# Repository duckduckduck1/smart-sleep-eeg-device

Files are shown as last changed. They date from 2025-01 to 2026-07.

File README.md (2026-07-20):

# Устройство ЭЭГ «Умного сна»

Прошивка и схемотехника ЭЭГ-устройства для нейробиологической лаборатории,
которая исследует сон на мышах.

Устройство снимает сигнал ЭЭГ аналоговым трактом на **MAX30003**, отдаёт его по
Bluetooth через модуль **JDY-16** и принимает обратно команды управления
фотобиомодуляцией — светом, которым воздействуют на животное. На другом конце —
[приложение оператора](https://github.com/duckduckduck1/smart-sleep-eeg-app),
которое пишет эксперимент на диск.

## Зачем это

Готовых ЭЭГ-регистраторов под мышь с нужным сочетанием требований нет: малый
вес на голове животного, автономное питание, беспроводная передача и
управляемый источник света в одном устройстве. Поэтому и плата, и прошивка
свои.

Репозиторий закрывает всё, что относится к железу: схемы трёх плат, прошивку
микроконтроллера и контракт обмена с приложением.

## Состав

Три платы, соединённые последовательно:

```text
Head_Mouse            MAX_V5              EEG_MASTER_REV2
(на голове мыши)  →  (аналоговый тракт) →  (МК, BLE, питание)  →  BLE → ПК
   электроды           MAX30003              STM32F103 + JDY-16
```

- **МК** — STM32F103C8T6.
- **Аналоговый тракт** — MAX30003, 250 Гц, связь по SPI.
- **Радио** — JDY-16 на UART, 9600 бод.
- **Питание** — литиевый аккумулятор, зарядка TP4056, стабилизаторы на 3,3 и
  1,8 В.

## С чего начать

**Чтобы собрать прошивку** нужны Visual Studio с
[VisualGDB](https://visualgdb.com/) и программатор ST-Link. Решение —
`firmware/visualgdb/smart-sleep-eeg-device.sln`, заливка по SWD.

При первой прошивке на новой машине почти наверняка потребуется поставить
драйвер WinUSB на ST-Link — как именно, описано
в [docs/firmware.md](docs/firmware.md#прошивка-не-идёт-error-open-failed).

**Чтобы открыть схемы** нужен Altium Designer. Проекты — в `hardware/`.

**Чтобы менять назначение ног** нужен
[STM32CubeMX](https://www.st.com/en/development-tools/stm32cubemx.html), файл
`firmware/EEG_sample.ioc`. Но прежде прочитайте про генерацию кода
в [docs/firmware.md](docs/firmware.md#не-перегенерировать-код-из-ioc): часть
логики дописана руками и генератор её перезапишет.

## Структура репозитория

```text
firmware/            прошивка STM32F103
  Core/              код от CubeMX и дописанная логика
  Drivers/           HAL и CMSIS от ST
  visualgdb/         проект VisualGDB и драйвер MAX30003
  EEG_sample.ioc     конфигурация CubeMX
hardware/            схемотехника, три проекта Altium
  EEG_MASTER_REV2/   основная плата: STM32, JDY-16, питание
  MAX_V5/            аналоговый тракт на MAX30003
  EEG_Head_Mouse V1/ головной модуль с электродами
docs/                документация
  firmware.md        сборка, распиновка, протокол, особенности
  hardware.md        платы и связь между ними
  datasheets/        документация на MAX30003 и STM32F103
```

## Документация

- [docs/firmware.md](docs/firmware.md) — как собирается прошивка, распиновка,
  протокол обмена с приложением, подводные камни.
- [docs/hardware.md](docs/hardware.md) — что за платы, из чего собраны, как
  связаны, что хранится в проектах Altium, а что нет.
- [CONTRIBUTING.md](CONTRIBUTING.md) — ветки, коммиты, что не коммитить.
- [Формат данных эксперимента](https://github.com/duckduckduck1/smart-sleep-eeg-app/blob/main/docs/data-format.md)
  — на стороне приложения: как декодировать отсчёты в микровольты. Контракт
  общий, поэтому здесь он не дублируется.

## Если что-то не работает

- **Проект не собирается после переноса файлов** — проверьте, что папка
  `firmware/` цела: проект VisualGDB тянет исходники относительными путями на
  два уровня вверх от себя.
- **Altium жалуется на недостающие библиотеки** — стандартные библиотеки
  компонентов в репозитории не хранятся, см.
  [docs/hardware.md](docs/hardware.md#что-лежит-в-проектах-а-что-нет). На уже
  размещённые элементы это не влияет.
- **Не прошивается, `Error: open failed`** — не установлен драйвер WinUSB на
  ST-Link. Лечится через Zadig, см.
  [docs/firmware.md](docs/firmware.md#прошивка-не-идёт-error-open-failed).
- **Устройство не находится по Bluetooth** — имя задаётся прошивкой командой
  `AT+NAMEEEG` при старте; ищите `EEG`.

Не нашли ответа — заведите
[issue](https://github.com/duckduckduck1/smart-sleep-eeg-device/issues).

## Кто поддерживает

Проект ведёт [@duckduckduck1](https://github.com/duckduckduck1) для конкретной
лаборатории. Изменения — через pull request, правила
в [CONTRIBUTING.md](CONTRIBUTING.md).

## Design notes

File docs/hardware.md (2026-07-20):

# Платы устройства

Описание трёх проектов Altium из `hardware/`: что за плата, из чего собрана и
как связана с остальными.

Состав восстановлен по схемам и библиотекам проектов. Где сведений в файлах не
нашлось, это отмечено прямо — лучше пробел, чем догадка, выданная за факт.

## Как платы связаны

```text
Head_Mouse            MAX_V5              EEG_MASTER_REV2
(на голове мыши)  →  (аналоговый тракт) →  (МК, BLE, питание)  →  BLE → ПК
   электроды           MAX30003              STM32F103 + JDY-16
```

Сигнал идёт от электродов на головном модуле в аналоговый тракт MAX30003,
оттуда по SPI в STM32, а из него по UART в модуль JDY-16 и дальше по BLE в
[приложение оператора](https://github.com/duckduckduck1/smart-sleep-eeg-app).

## EEG_MASTER_REV2 — основная плата

Несёт микроконтроллер, радиомодуль и питание. Схема разбита на четыре листа.

| лист | что на нём |
|---|---|
| `Main.SchDoc` | сборка листов, отладочный разъём SWD |
| `STM32.SchDoc` | STM32F103, модуль **JDY-16**, транслятор уровней **BSS138**, светодиод |
| `Power.SchDoc` | зарядка **TP4056**, стабилизаторы **RT9013-33GB** (3,3 В) и **RT9013-18GB** (1,8 В) |
| `Connectors.SchDoc` | разъёмы **BM10B-SRSS-TB** (JST, 10 контактов) к плате MAX30003 |

Два стабилизатора не случайны: цифровая часть MAX30003 питается от 1,8 В, а
STM32 и радиомодуль — от 3,3 В. Отсюда же и BSS138 — согласование уровней между
доменами.

Наличие TP4056 означает питание от литиевого аккумулятора с зарядкой по USB.

Файлы плат: `EEG_Master_Rev2.PcbDoc`, `EEG_MASTER_REV2(2).PcbDoc`,
`ALL_PCB.PcbDoc`. Какая из трёх версий актуальна — из файлов не следует.

## MAX_V5 — аналоговый тракт

Плата с **MAX30003**: снимает сигнал с электродов и отдаёт его по SPI.
Схема — `Sheet2.SchDoc`, плата — `PCB2.PcbDoc`.

Параметры тракта, от которых зависит перевод отсчётов в микровольты
(`V_REF = 1.0 В`, `GAIN = 160`), описаны на стороне приложения:
[docs/data-format.md](https://github.com/duckduckduck1/smart-sleep-eeg-app/blob/main/docs/data-format.md).

## EEG_Head_Mouse V1 — головной модуль

Плата, которая ставится на голову животного и держит электроды.
Схема — `Sheet1.SchDoc`, плата — `PCB1.PcbDoc`.

Из схемы состав вытащить не удалось — текстовых обозначений в файле нет. По
библиотекам проекта видно, что используются микроразъёмы **SAMTEC** серии DWM
(`DWM-03-X-X-S-X`, `DWM-04-60-G-S-625`) — типовой выбор для съёмного соединения
с головным имплантом.

## Что лежит в проектах, а что нет

В репозитории то, без чего проект не открыть и плату не повторить: схемы,
платы, файлы проектов, BOM, задания вывода и библиотеки под конкретные
компоненты.

Не хранится то, что Altium делает сам:

| не хранится | почему |
|---|---|
| `History/` | собственный контроль версий Altium — снимки тех же файлов, которые уже версионирует git |
| `Project Outputs for *` | герберы, сверловка, PDF — генерируются из проекта |
| `Project Logs for *` | журналы работы Altium |
| `__Previews/` | миниатюры предпросмотра |
| `IntegratedLibrary/` | стандартные библиотеки резисторов, конденсаторов, пассивки, транзисторов — общие, ставятся с Altium |

Из-за этого при первом открытии проекта Altium может пожаловаться на
недостающие библиотеки для типовых компонентов. На уже размещённые элементы это
не влияет: их данные лежат в самих схемах и платах. Библиотеки нужны только
чтобы **добавлять новые** типовые компоненты — тогда подключите стандартные
библиотеки Altium.

## Даташиты

`docs/datasheets/` — документация на две ключевые микросхемы:

- `max30003.pdf` — аналоговый тракт, карта регистров, формат FIFO;
- `stm32f103c8.pdf` — микроконтроллер.

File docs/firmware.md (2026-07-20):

# Прошивка

Подробности по прошивке STM32F103: как собирается, распиновка, обмен с
приложением оператора и особенности, о которых стоит знать заранее.

Общее описание проекта — в [README.md](../README.md), платы —
в [hardware.md](hardware.md).

## Как собирается

Два инструмента, у каждого своя роль:

1. **STM32CubeMX** — назначение ног и периферии. По файлу `EEG_sample.ioc` он
   генерирует код инициализации на HAL: `Core/Src/gpio.c`, `spi.c`, `tim.c`,
   `usart.c`, `dma.c` и каркас `main.c`.
2. **VisualGDB в Visual Studio** — сборка и прошивка. Сгенерированный проект
   импортируется сюда, и дальше вся работа идёт в нём.

Решение — `firmware/visualgdb/smart-sleep-eeg-device.sln`. Проект собирает
исходники из `firmware/Core/`, поднимаясь на два уровня вверх от своего файла,
плюс лежащий рядом драйвер `max30003.c`. Прошивка заливается по SWD
(ноги PA13/PA14).

> **STM32CubeIDE в работе не используется.** Файлы `.cproject`, `.project`,
> `.settings` и `.mxproject` — побочный продукт CubeMX: он создаёт их, потому
> что в качестве тулчейна выбран CubeIDE. Собрать по ним проект не получится
> (драйвер MAX30003 не входит в их пути включения), но это ничего не значит —
> ими никто не пользуется. Удалять их тоже незачем: CubeMX создаст их заново.

### Что понадобится

| | где взять |
|---|---|
| **STM32CubeMX** | [st.com](https://www.st.com/en/development-tools/stm32cubemx.html) — бесплатно, нужна регистрация |
| **Visual Studio** | достаточно редакции Community |
| **VisualGDB** | [visualgdb.com](https://visualgdb.com/) — платный, есть пробный период и отдельная лицензия для некоммерческого использования |
| **ST-Link** | программатор, подключается к PA13/PA14 |

## Прошивка не идёт: `Error: open failed`

Самая частая беда при настройке на новой машине. В логе выглядит так:

```text
Warn : DEPRECATED: auto-selecting transport "swd (dapdirect)".
Error: open failed
```

Это **не проблема платы, проводов или прошивки**. OpenOCD не смог открыть сам
программатор — ошибка возникает до того, как он доберётся до микроконтроллера.
Если бы дело было в SWD или в питании платы, сообщение было бы другим:
`init mode failed (unable to connect to the target)`.

Причина почти всегда одна: **к ST-Link не привязан драйвер WinUSB**. Проверить
можно в диспетчере устройств — устройство видно, но без класса и с кодом
ошибки 28, «драйверы для устройства не установлены».

### Как лечится

Поставить WinUSB-драйвер на ST-Link через [Zadig](https://zadig.akeo.ie/):

1. Подключить ST-Link.
2. Запустить Zadig **от имени администратора**.
3. Если ST-Link не виден в списке — `Options` → `List All Devices`.
4. Выбрать **STM32 STLink** (идентификатор `USB\VID_0483&PID_3748`).
5. В поле целевого драйвера выбрать **WinUSB**, нажать `Replace Driver`.
6. Переподключить ST-Link и запустить отладку заново.

В поставке VisualGDB есть своя утилита для того же — `UsbDriverTool.exe`
в папке установки. Она проще, но срабатывает не всегда; Zadig надёжнее.

> **Официальный драйвер ST (STSW-LINK009) для этого не подходит.** Он
> привязывает устройство к своему стеку, а OpenOCD работает через libusb и
> ждёт WinUSB. С драйвером ST программатор будет виден в утилитах ST, но
> VisualGDB его не откроет.

## Распиновка

| нога | назначение |
|---|---|
| PA5 | SPI1_SCK — MAX30003 |
| PA6 | SPI1_MISO — MAX30003 |
| PA7 | SPI1_MOSI — MAX30003 |
| PA4 | CS для MAX30003 — обрамляет транзакции макросами `NSS_down` / `NSS_up` |
| PA9 | USART1_TX — в JDY-16 |
| PA10 | USART1_RX — из JDY-16 |
| PA1 | TIM2_CH2 — **FCLK**, тактирование MAX30003, включается макросом `FCLK_on` |
| PA2 | TIM2_CH3 — ШИМ светодиода ФБМ (**в `.ioc` не описана**) |
| PA13 / PA14 | SWDIO / SWCLK — отладка и прошивка |

Периферия:

- **SPI1** — мастер, 8 бит, CPOL 0 / CPHA 0, NSS программный (нога PA4).
- **USART1** — 9600 бод, 8N1, приём по прерыванию, по одному байту.
- **TIM2** — предделитель 0, период 249. Заняты **оба** канала: канал 2 даёт
  тактовый сигнал MAX30003, канал 3 — ШИМ светодиода.
- **TIM3** — предделитель 8, период 1000.

Макросы `FCLK_on` / `FCLK_off` и `NSS_up` / `NSS_down` объявлены
в `max30003.h` и разворачиваются в работу с TIM2 и ногой PA4. По имени ноги
её назначение не найти — искать надо по макросу.

## Обмен с приложением

### Поток отсчётов

250 Гц, один отсчёт — три байта. Прошивка копит 12 отсчётов и отдаёт их одним
пакетом в 36 байт в UART, откуда их забирает JDY-16 и отправляет по BLE.

Формат отсчёта и его декодирование в микровольты описаны на стороне приложения
и здесь не дублируются:
[docs/data-format.md](https://github.com/duckduckduck1/smart-sleep-eeg-app/blob/main/docs/data-format.md).

> **Запас по скорости почти исчерпан.** 250 Гц × 3 байта = 750 Б/с, а UART на
> 9600 бод даёт 960 Б/с — занято около 78 %. Добавить в поток что-то ещё без
> повышения скорости не выйдет.

### Команда управления светом

Приходит по тому же UART, четыре байта:

```text
[on_off, pwm, 0x0D, 0x0A]
```

| байт | значение |
|---|---|
| `on_off` | `0x01` — включить ШИМ, `0x00` — выключить |
| `pwm` | скважность, **0…249** |
| `0x0D 0x0A` | обязательный конец пакета |

Разбирает команду `HAL_UART_RxCpltCallback` в `Core/Src/main.c`: байты копятся
до пары `0x0D 0x0A`, после чего пакет длиной ровно 4 байта принимается
к исполнению, остальные отбрасываются.

## Особенности

### Шкала ШИМ не совпадает с приложением

Период TIM2 равен 249, то есть полная яркость — это `pwm = 249`, и всё, что
больше, прошивка обрезает до 249. Приложение же считает
`pwm = round(уровень × 255 / 100)`.

В результате уровни 98 % и 99 % дают ту же яркость, что и ~97,6 %. Расхождение
небольшое и на работу не влияет — **исправлять его не планируется**, но при
разборе данных стоит помнить: яркость выше ~97 % не различается.

### Не перегенерировать код из `.ioc`

Часть логики дописана руками в файлах, которыми владеет CubeMX, и лежит вне
секций `USER CODE`:

| файл | что пропадёт при генерации |
|---|---|
| `Core/Src/main.c` | приём команд, настройка MAX30003, цикл чтения отсчётов, `SetDuty()` — маркеры `USER CODE` из файла удалены, осталась одна секция в самом конце |
| `Core/Src/tim.c` | настройка TIM2 канала 3 и инициализация ноги PA2 — вставлены между сгенерированными блоками |

Ноги давно назначены и переназначать их не нужно, так что на практике это не
мешает. Если всё же понадобится — сначала сохраните `main.c` и `tim.c`, потом
верните свои куски обратно.

### `.ioc` знает не про все ноги

В `.ioc` описан канал 2 TIM2 на ноге PA1 — это FCLK, и он верен. А канала 3 на
ноге PA2, который даёт ШИМ светодиода, там нет: он дописан руками прямо
в `tim.c`. Источник правды по ШИМ — код, не `.ioc`.

### Драйвер MAX30003 лежит внутри проекта VisualGDB

`max30003.c` и `max30003.h` лежат в `firmware/visualgdb/smart-sleep-eeg-device/`
— рядом с файлом проекта, а не вместе с остальными исходниками в `Core/`.
Из-за этого кажется, что проектов два. Проект **один**: `.vcxproj` собирает
и `Core/`, и драйвер.

Переносить драйвер в `Core/` никто не мешает, но это правка путей в файле
проекта, то есть риск сломать сборку — а работающую прошивку трогать без
надобности не стоит.

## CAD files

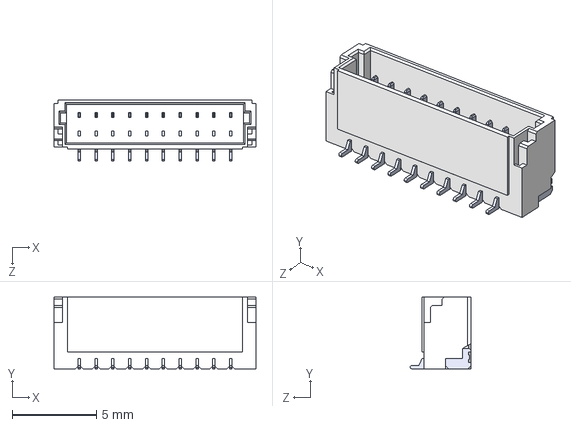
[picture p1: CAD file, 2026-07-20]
hardware/EEG_MASTER_REV2/Библиотеки/STEP/BM10B-SRSS-TB -LF--SN---3DModel-STEP-56544.STEP
12.0 x 4.25 x 3.60 mm

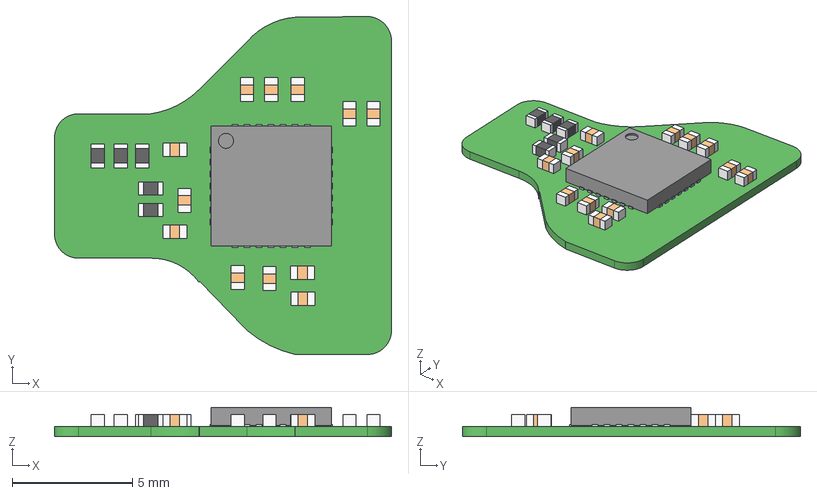
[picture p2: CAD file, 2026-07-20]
hardware/MAX_V5/PCB2.step
14.0 x 14.0 x 1.21 mm
Extruded x 51
ThermalPin
PinsArrayLR
PinsArrayTB

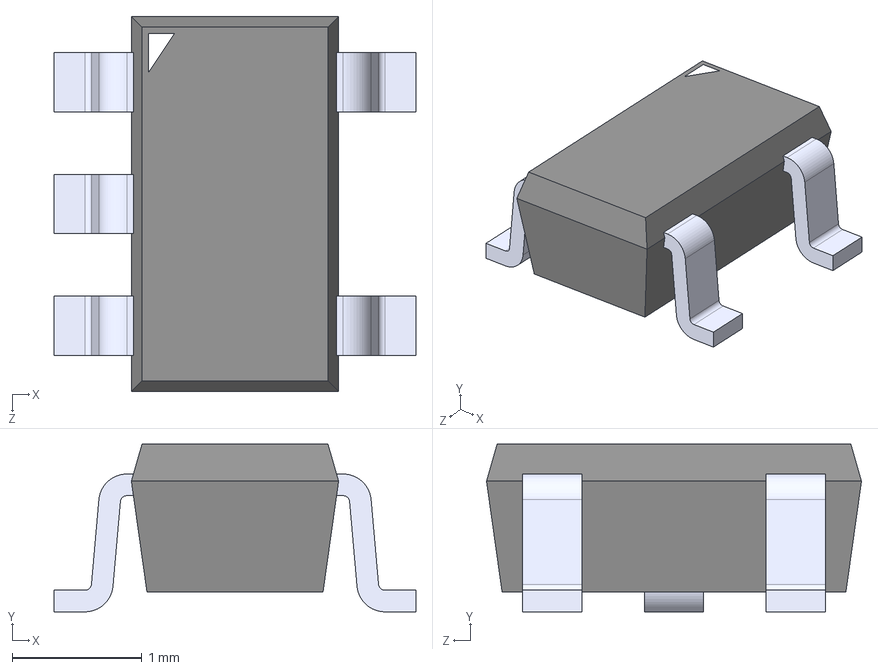
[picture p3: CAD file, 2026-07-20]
hardware/EEG_MASTER_REV2/Библиотеки/STEP/RT9013-33GB.STEP
2.79 x 1.30 x 2.90 mm

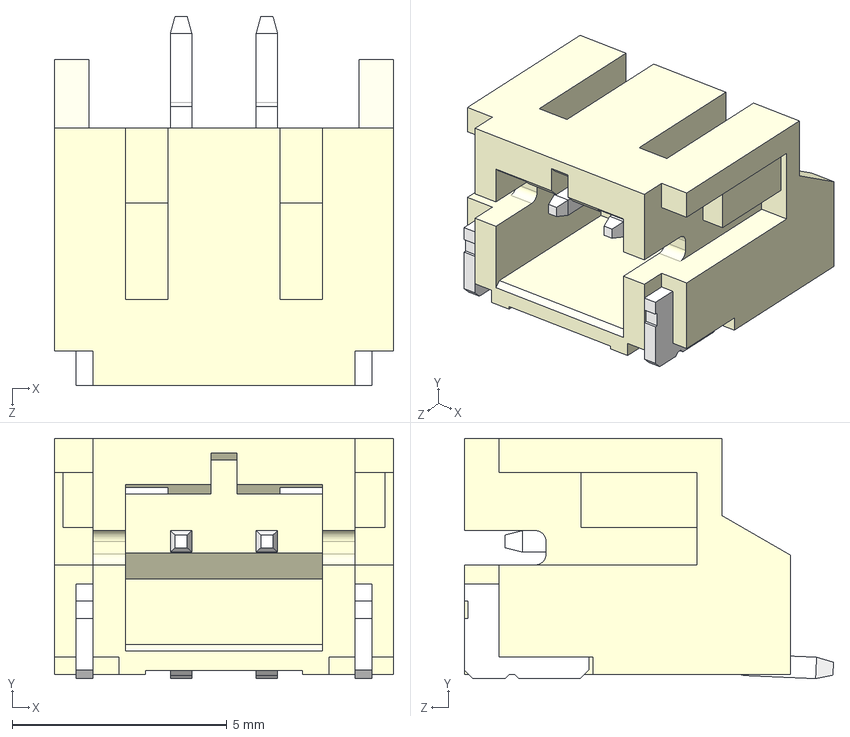
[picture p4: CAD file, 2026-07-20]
hardware/EEG_MASTER_REV2/Библиотеки/STEP/S2B-PH-SM4-TB(LF)(SN)--3DModel-STEP-56544.STEP
7.90 x 5.60 x 8.60 mm

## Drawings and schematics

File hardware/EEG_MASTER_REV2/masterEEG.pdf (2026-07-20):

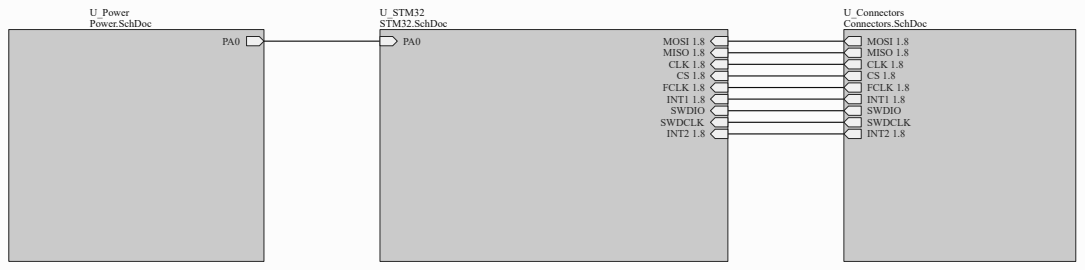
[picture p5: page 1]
Title; Size; Number; Revision; Date:; Sheet of; File:; C:\Сергей Попов\..\Main.SchDoc; Drawn By:; U_Power Power.SchDoc; MOSI 1.8 MISO 1.8 CLK 1.8 CS 1.8 FCLK 1.8; SWDIO SWDCLK; INT1 1.8; INT2 1.8; U_STM32 STM32.SchDoc; MISO 1.8; MOSI 1.8; CLK 1.8 CS 1.8 FCLK 1.8 INT1 1.8 SWDIO SWDCLK INT2 1.8; U_Connectors Connectors.SchDoc

# R2 ⁰.063W ¹% 100KOm

# VOLTAGE REGULATOR

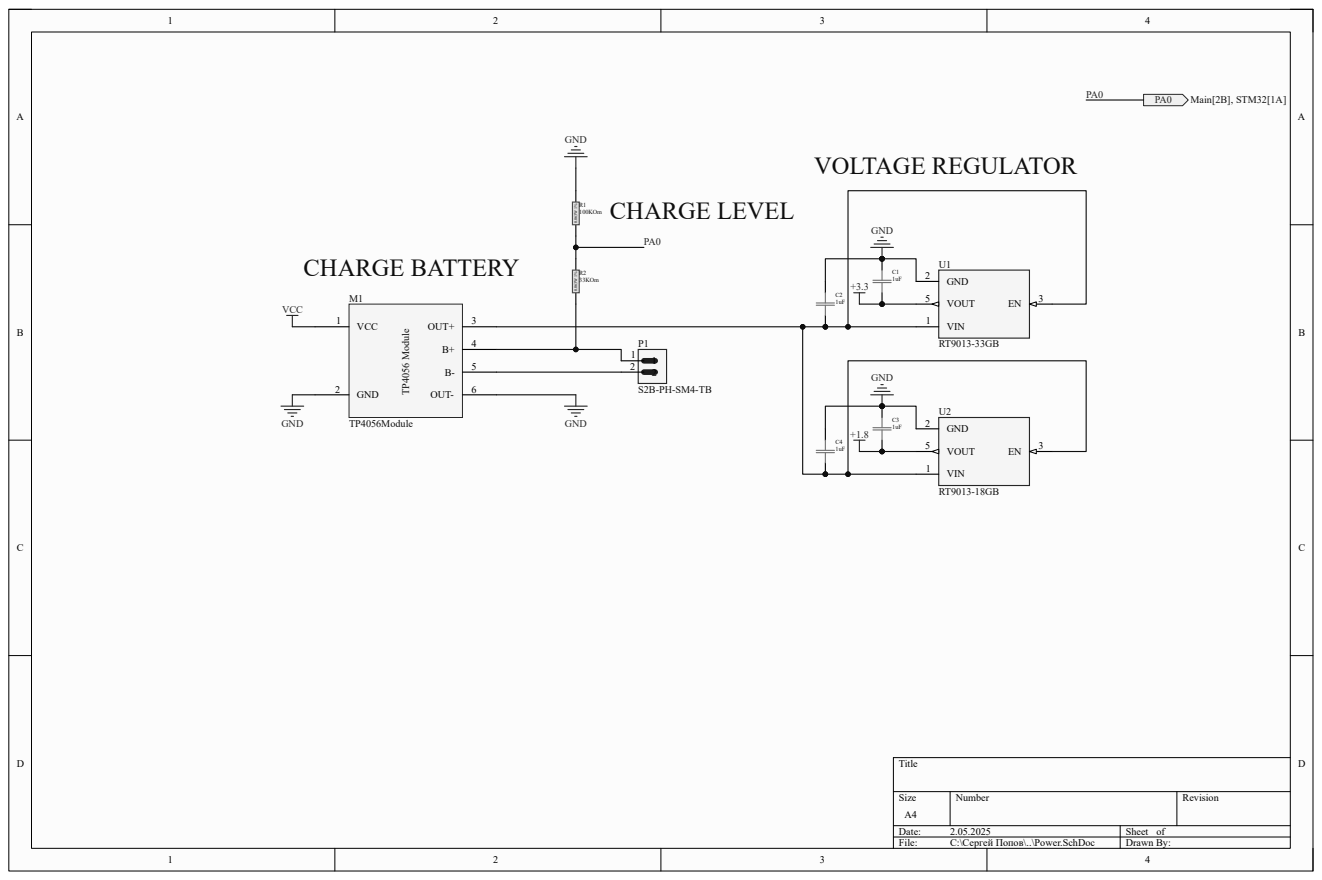
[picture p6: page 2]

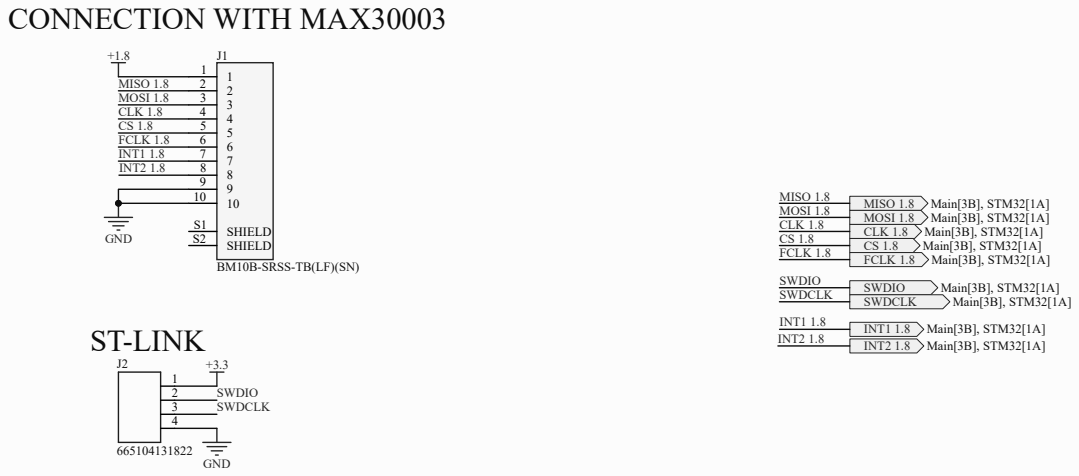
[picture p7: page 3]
Title; Size; Number; Revision; File:; C:\Сергей Попов\..\Connectors.SchDoc; Drawn By:; GND; SHIELD S1 SHIELD S2; MISO 1.8 MOSI 1.8 CLK 1.8 CS 1.8 FCLK 1.8 INT1 1.8; SWDIO SWDCLK; MISO 1.8 Main[3B], STM32[1A] MOSI 1.8 Main[3B], STM32[1A] CLK 1.8 Main[3B], STM32[1A]; Main[3B], STM32[1A]; FCLK 1.8 Main[3B], STM32[1A]; INT1 1.8 Main[3B], STM32[1A]; SWDIO; SWDCLK; CONNECTION WITH MAX30003; ST-LINK; INT2 1.8; INT2 1.8 Main[3B], STM32[1A]; MISO 1.8 MOSI 1.8 CLK 1.8 CS 1.8 FCLK 1.8; INT1 1.8 INT2 1.8

BM10B-SRSS-TB(LF)(SN)

# INDICATION

# LOGIC LEVEL

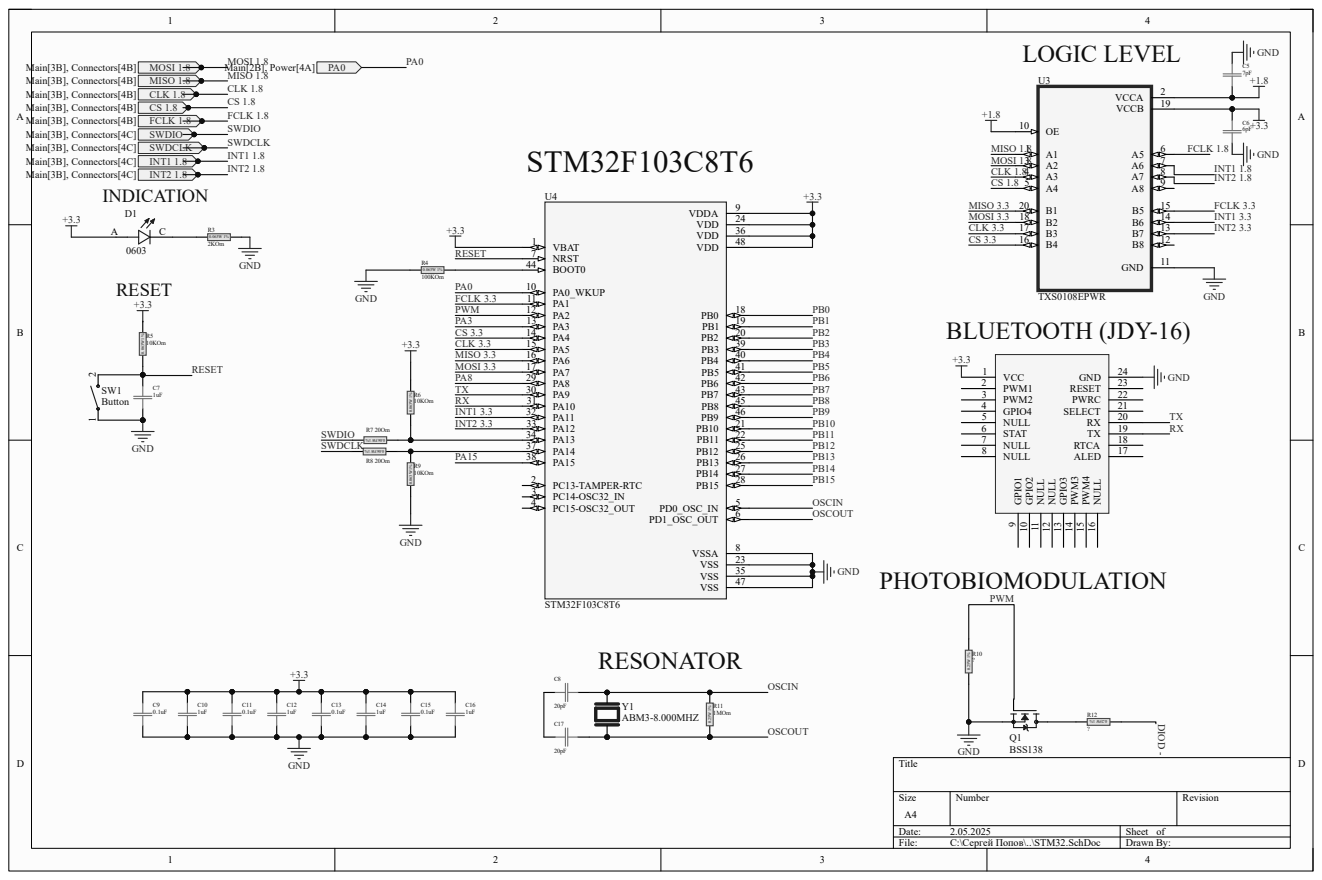
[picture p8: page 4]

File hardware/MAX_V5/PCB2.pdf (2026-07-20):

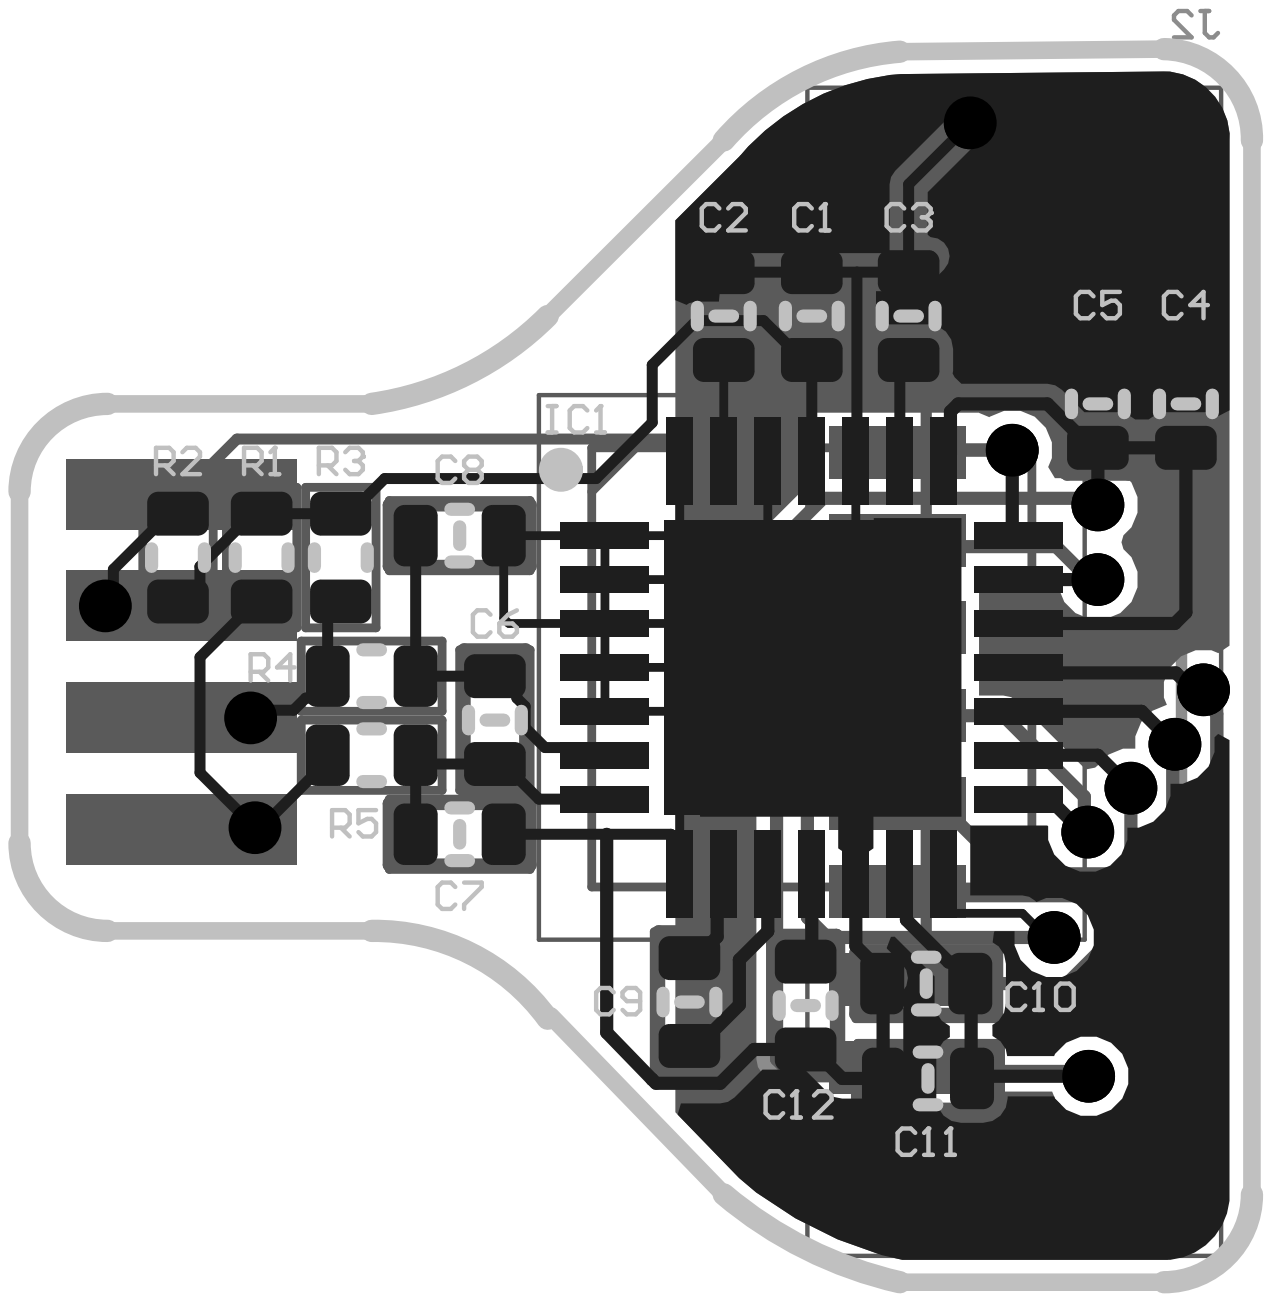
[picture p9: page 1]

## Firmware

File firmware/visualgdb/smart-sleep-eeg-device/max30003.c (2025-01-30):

#include "main.h"





static uint8_t RST[4] = { 0x00, 0x00, 0x00, 0x00 };
void MAX_WREG(uint8_t REG, uint8_t *data) //Запись в регистр 
{
	uint8_t cmdBuffer[4];
	cmdBuffer[0] = (REG << 1) | WREG;
	for (int i = 1; i < 4; i++)
	{
		cmdBuffer[i] = *(data + i);
	} 
	NSS_down;
	HAL_SPI_Transmit(&hspi1, cmdBuffer, 4, 10);

	NSS_up;
}

void MAX_RREG(uint8_t REG, uint8_t *rxBuff) // Чтение Регистра 
{
	
	uint8_t txBuff = (REG << 1) | RREG;
	NSS_down;
	HAL_SPI_Transmit(&hspi1, &txBuff, 1, 0);
	HAL_SPI_Receive(&hspi1, rxBuff, 3, 10);
	NSS_up;
}

void MAX_CNFG_GEN_init(struct CNFG_GEN_init reg)
{
	//формирование иструкции инициализации////////////////////
	uint8_t buf[4] = { 0, 0, 0, 0 };
	buf[3] =  reg.RBIASN << 0 //  первого байта регистра CNFG_GEN - [0:7]
			| reg.RBIASP << 1 
			| reg.RBIASV << 2
			| reg.EN_RBIAS << 4
			| reg.DCLOFF_VTH << 6;
	buf[2] = reg.DCLOFF_IMAG << 0 //  второго байта регистра CNFG_GEN - [8:15]
			| reg.DCLOFF_IPOL << 3
			| reg.EN_DCLOFF << 4;
			
	buf[1] = reg.EN_ECG << 3 // Третьего байта регистра CNFG_GEN - [16:23]
			| reg.FMSTR << 4
			| reg.EN_ULP_LON << 6;
	MAX_WREG(CNFG_GEN, buf);
	
}

struct CNFG_GEN_init MAX_CNFG_GEN_read()
{
	struct CNFG_GEN_init cfg;
	uint8_t rxBuf[4] = { 0, };
	MAX_RREG(CNFG_GEN, rxBuf); //Читаем регистр в rxBuf
	// Записываем первый байт/////////////////////////
	cfg.RBIASN = rxBuf[2];  
	cfg.RBIASP = rxBuf[2];
	cfg.RBIASV = rxBuf[2];
	cfg.EN_RBIAS = rxBuf[2];
	cfg.DCLOFF_VTH = rxBuf[2];
	
	cfg.RBIASN  = (cfg.RBIASN & 0x01) >> 0;  
	cfg.RBIASP = (cfg.RBIASP & 0x02) >> 1; 
	cfg.RBIASV = (cfg.RBIASV & 0x0C) >> 2;
	cfg.EN_RBIAS = (cfg.EN_RBIAS & 0x30) >> 4;
	cfg.DCLOFF_VTH = (cfg.DCLOFF_VTH & 0xC0) >> 6;
	
	//Записываем второй байт//////////////////////
	
	cfg.DCLOFF_IMAG = rxBuf[1];
	cfg.DCLOFF_IPOL = rxBuf[1];
	cfg.EN_DCLOFF =  rxBuf[1];
		
	cfg.DCLOFF_IMAG = (cfg.DCLOFF_IMAG & 0x07) >> 0;
	cfg.DCLOFF_IPOL = (cfg.DCLOFF_IPOL & 0x08)  >> 3;
	cfg.EN_DCLOFF = (cfg.EN_DCLOFF & 0x30) >> 4;
	
	//Записываем третий байт//////////////////////// 
	
	cfg.EN_ECG = rxBuf[0];
	cfg.FMSTR = rxBuf[0];
	cfg.EN_ULP_LON = rxBuf[0];
	
	cfg.EN_ECG = (cfg.EN_ECG & 0x08) >> 3;
	cfg.FMSTR = (cfg.FMSTR & 0x30) >> 4;
	cfg.EN_ULP_LON = (cfg.EN_ULP_LON & 0xC0) >> 6;
	
	////////////////////////////////////////////////
	
	return cfg;
};

void MAX_CNFG_ECG_init(struct CNFG_ECG_init reg) 
{ 
	uint8_t buf[4] = { 0, 0, 0, 0 };
	buf[2] = reg.DLPF << 4
			| reg.DHPF << 6;
	buf[1] = reg.GAIN << 0
			| reg.RATE << 6;
	MAX_WREG(CNFG_ECG, buf);		
}

struct CNFG_ECG_init MAX_CNFG_ECG_read()
{
	struct CNFG_ECG_init reg;
	uint8_t rxBuf[4] = { 0, }; 
	MAX_RREG(CNFG_ECG, rxBuf); //Читаем регистр в rxBuf
	//Записываем первый байт///////////////////////////
	reg.DHPF = rxBuf[1]; 
	reg.DLPF = rxBuf[1];
	
	reg.DLPF = (reg.DLPF & 0x30) >> 4;
	reg.DHPF = (reg.DHPF & 0x40) >> 6;
	
	//Забисываем второй байт////////////////////////// 
	reg.GAIN = rxBuf[0];
	reg.RATE = rxBuf[0];
	
	reg.GAIN = (reg.GAIN & 0x03) >> 0;
	reg.RATE = (reg.RATE & 0xC0) >> 6;
	
	//////////////////////////////////////////////////
	
	return reg;
};

void MAX_MNGR_DYN_init(struct MNGR_DYN_init cfg)
{
	uint8_t buf[4] = { 0, 0, 0, 0 };
	buf[1] = cfg.FAST_TH << 0
			| cfg.FAST << 6;
	MAX_WREG(MNGR_DYN, buf);
}

struct MNGR_DYN_init MAX_MNGR_DYN_read()
{
	struct MNGR_DYN_init reg = {};
	uint8_t rxBuf[4] = { 0, }; 
	MAX_RREG(MNGR_DYN, rxBuf); //Читаем регистр в rxBuf
	
	reg.FAST_TH = rxBuf[0];
	reg.FAST = rxBuf[0];
	
	reg.FAST_TH = (reg.FAST_TH & 0x3F) >> 0;
	reg.FAST = (reg.FAST & 0xC0) >> 6;
	return reg;
	
};

void MAX_CNFG_CAL_init(struct CNFG_CAL_init cfg)
{
	uint8_t buf[4] = { 0, 0, 0, 0 };
	
	buf[3] = cfg.THIGH_L;
	
	buf[2] = cfg.THIGH_H << 0
			| cfg.FIFTY << 3
			| cfg.FCAL << 4;
	
	buf[1] = cfg.VMAG << 4
			| cfg.VMODE << 5
			| cfg.EN_VCAL << 6;
	MAX_WREG(CNFG_CAL, buf);
}

struct CNFG_CAL_init MAX_CNFG_CAL_read()
{
	struct CNFG_CAL_init reg = { };
	uint8_t rxBuf[4] = { 0, }; 
	MAX_RREG(CNFG_CAL, rxBuf); //Читаем регистр в rxBuf
	//Записываем первый байт///////////////////////////
	reg.THIGH_L = rxBuf[2];
	
	//Забисываем второй байт////////////////////////// 
	reg.THIGH_H = rxBuf[1];
	reg.FIFTY = rxBuf[1];
	reg.FCAL = rxBuf[1];
	
	reg.THIGH_H = (reg.THIGH_H & 0x07) >> 0;
	reg.FIFTY = (reg.FIFTY & 0x08) >> 3;
	reg.FCAL = (reg.FCAL & 0x70) >> 4;
	
	//Забисываем третий байт////////////////////////// 
	reg.VMAG = rxBuf[0];
	reg.VMODE = rxBuf[0];
	reg.EN_VCAL = rxBuf[0]; 
	
	reg.VMAG = (reg.VMAG & 0x10) >> 4;
	reg.VMODE = (reg.VMODE & 0x20) >> 5;
	reg.EN_VCAL = (reg.EN_VCAL & 0x40) >> 6;
	
	
	return reg;
}; 

void  MAX_CNFG_EMUX_init(struct CNFG_EMUX_init cfg) 
{ 
	uint8_t buf[4] = { 0, 0, 0, 0 };
	
	buf[1] = cfg.CALN_SEL << 0
			| cfg.CALP_SEL << 2
			| cfg.OPENN << 4
			| cfg.OPENP << 5
			| cfg.POL << 7;
	MAX_WREG(CNFG_EMUX, buf);
}

struct CNFG_EMUX_init MAX_CNFG_EMUX_init_read()
{
	struct  CNFG_EMUX_init reg = { };
	uint8_t rxBuf[4] = { 0, }; 
	MAX_RREG(CNFG_EMUX, rxBuf); //Читаем регистр в rxBuf
	reg.CALN_SEL = rxBuf[0];
	reg.CALP_SEL = rxBuf[0];
	reg.OPENN = rxBuf[0];
	reg.OPENP = rxBuf[0];
	reg.POL = rxBuf[0];
	
	reg.CALN_SEL = (reg.CALN_SEL & 0x03) >> 0;
	reg.CALP_SEL = (reg.CALP_SEL & 0x0C) >> 2;
	reg.OPENN = (reg.OPENN & 0x01) >> 4;
	reg.OPENP = (reg.OPENP & 0x20) >> 5;
	reg.POL = (reg.POL & 0x80) >> 7;
	
	return reg;
};

struct RO_STATUS MAX_Status_read()
{
	struct  RO_STATUS status = { };
	uint8_t rxBuf[4] = { 0, }; 
	MAX_RREG(CNFG_CAL, rxBuf); //Читаем регистр в rxBuf
	
	status.LDOFF_NL = rxBuf[2];
	status.LDOFF_NH = rxBuf[2];
	status.LDOFF_PL = rxBuf[2];
	status.LDOFF_PH = rxBuf[2];
	
	status.LDOFF_NL = (status.LDOFF_NL & 0x01) >> 0;
	status.LDOFF_NH = (status.LDOFF_NH & 0x02) >> 1;
	status.LDOFF_PL = (status.LDOFF_PL & 0x04) >> 2;
	status.LDOFF_PH = (status.LDOFF_PH & 0x08) >> 3;
	
	status.PLLINT = rxBuf[1];
	status.SAMP = rxBuf[1];
	status.RRINT = rxBuf[1];
	status.LONINT = rxBuf[1];
	
	status.PLLINT = (status.PLLINT & 0x01) >> 0;
	status.SAMP = (status.SAMP & 0x02) >> 1;
	status.RRINT = (status.RRINT & 0x04) >> 2;
	status.LONINT = (status.LONINT & 0x08) >> 3;
	
	status.DCLOFFINT = rxBuf[0];
	status.FSTINT = rxBuf[0];
	status.EOVF = rxBuf[0];
	status.EINT = rxBuf[0];
	
	status.DCLOFFINT = (status.DCLOFFINT & 0x10) >> 4;
	status.FSTINT = (status.FSTINT & 0x20) >> 5;
	status.EOVF = (status.EOVF & 0x40) >> 6; 
	status.EINT = (status.EINT & 0x80) >> 7;
	
	return status;
	
};

void  MAX_EN_INT_init(struct EN_INT_init cfg, uint8_t intNuber) 
{ 
	uint8_t buf[4] = { 0, 0, 0, 0 };
	
	buf[3] = cfg.INTB_TYPE << 0;
	buf[2] = cfg.EN_PLLINT 
			| cfg.EN_SAMP << 1
			| cfg.EN_RRINT << 2
			| cfg.EN_LONINT << 3;
	
	buf[1] = cfg.EN_DCLOFFINT << 4
			| cfg.EN_FSTINT << 5
			| cfg.EN_EOVF << 6
			| cfg.EN_EINT << 7;	
	switch (intNuber)
	{
	case 1:
		MAX_WREG(EN_INT, buf);
		break;
	case 2:
		MAX_WREG(EN_INT2, buf);
	default:
		break;
	}
	
}
static uint8_t MAX_GetEtag(uint8_t *fifo)
{
	uint8_t eTag = (*(fifo + 2) &= 0x38) >> 3;
	return eTag;
}

static uint8_t MAX_GetPtag(uint8_t *fifo)
{
	uint8_t pTag = (*(fifo + 2) &= 0x07) >> 0;
	return pTag;
}

uint32_t MAX_GetData(uint8_t *fifo)
{
	uint32_t data1 = (*(fifo) << 16);
	uint32_t data2 = (*(fifo + 1) << 8);
	uint32_t data3 = (*(fifo + 2));
	uint32_t data = data1 | data2 | data3;
	data = data >> 6;
	return data;
}
uint32_t  MAX_readFIFO()
{
	uint8_t rawData[4] = { 0, };
	MAX_RREG(ECG_FIFO_BURST, rawData);
	if ((MAX_GetEtag(rawData) == 0x02) || (MAX_GetEtag(rawData) == 0x00) || (MAX_GetPtag(rawData) == 0x00) || (MAX_GetPtag(rawData) == 0x02))
	{
		HAL_UART_Transmit(&huart1, rawData, 3 , 10);
		uint32_t data = MAX_GetData(rawData);
		return data;
	}
	else
	{
		MAX_FIFO_RESET();
		return 0;
	}
}
void MAX_FIFO_RESET()
{
	MAX_WREG(FIFO_RST, RST);
}

void MAX_SYNCH()
{
	MAX_WREG(SYNCH, RST);
}

void MAX_SW_RESET()
{
	MAX_WREG(SW_RST, RST);
}

signed int PositiveToNegative(uint32_t data)
{
	signed int signedData = data;
	if (data > 131072)
	{
		signedData = ((data ^= 0x3FFFF) + 1) * -1;
		
	}
	
	
	
	return signedData;
}

void MAX_WriteToBuff(uint32_t *buff , uint16_t counter)
{
		uint8_t temp[3] = { 0, };
		MAX_RREG(ECG_FIFO, temp);
		buff[counter] = MAX_GetData(temp);
}

static void in32ToByteArray(uint32_t val, uint8_t *buff)
{
	buff[0] = val >> 16;
	buff[1] = (val >> 8);
	buff[2] = (val >> 0);
}

void clearBuff(uint8_t *buff, uint16_t size)
{
	for (uint16_t i = 0; i < size; i++)
	{
		buff[i] = 0;
	}
}
void MAX_Transmit_sample(uint32_t *buff, uint8_t size)
{
	uint8_t temp[3] = { 0, };
	for (uint8_t i = 0; i < size; i++)
	{
		in32ToByteArray(buff[i], temp);
		HAL_UART_Transmit_DMA(&huart1, temp, 3);
		clearBuff(temp, 3);
	}
}

uint8_t FifoReadyCheck()
{
	uint8_t temp[3] = { 0, };
	MAX_RREG(STATUS, temp);
	if ((temp[0] &= 0x80) == 0x80)
	{
		return 1;
	}
	else
	{
		return 0;
	}
}

uint8_t CheckEtag(uint8_t sample)				
{												
	return (sample >> 3) & 0x07;						
			 
}

void MAX_WriteBuff_8bit(uint8_t *buff, uint16_t count)
{
	uint8_t temp[3] = { 0, };

		MAX_RREG(ECG_FIFO, temp);
		uint8_t  etag = CheckEtag(temp[2]);
	if (etag == EtagValid || etag == EtagLastValid)
	{		
			for (uint16_t j = 0; j < 3; j++)
			{
				buff[(3*count + j)] = temp[j]; 
			}				
		
	}
	

	
		
		//clearBuff(temp, 3);
	
}
